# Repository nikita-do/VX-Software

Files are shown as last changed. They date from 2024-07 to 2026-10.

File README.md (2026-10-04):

# Vital-X Software

Vital-X streams ECG, PPG, and EDA/GSR measurements to a Python backend over MQTT. The backend processes the incoming signals, estimates a pain level, and stores measurements for monitoring and later review.

This repository contains the server backend and presentation materials. The project describes a mobile-friendly web interface hosted separately; its source code is  present `software/vitalx_site/`.

## Demo

[Open or download the demo video](https://dvn-resume.vercel.app/assets/projects/vitallog/demo.mp4) (`assets/output.mp4`).

## System Overview

The device sends CBOR-encoded data through an MQTT broker. The backend subscribes to device topics, decodes and validates packets, and passes the signal batches through preprocessing and pain assessment. Raw and processed signals, extracted features, and pain estimates are written to InfluxDB. Pain and pulse-rate estimates are also published over MQTT. When measurement stops, the logger exports processed data to CSV and attempts an optional Google Drive upload; Drive upload is not verified as ready to use without additional setup.

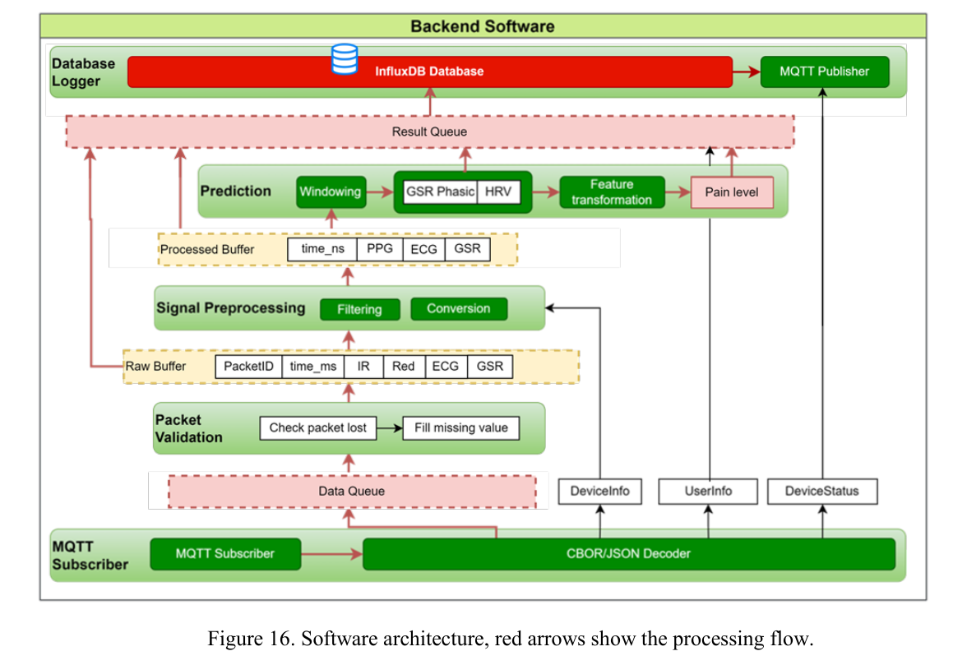
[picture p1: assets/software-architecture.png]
Vital-X backend software architecture and processing flow


The MQTT topic map below shows the device, server, and client communication.

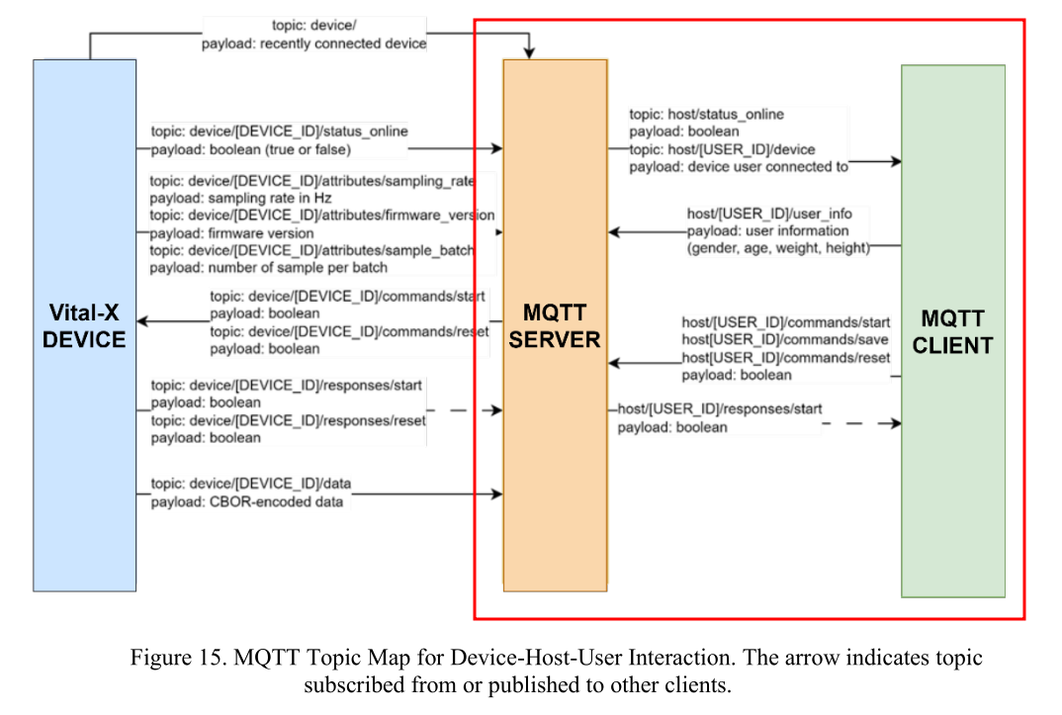
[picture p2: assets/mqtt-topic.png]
Vital-X MQTT topic map


## Remote Device Control

The device is controlled through the [Vital-X web interface](https://vitalx-site.vercel.app/). The device-specific URLs is specified in the `?device=DEVICE_ID` query parameter; replace `DEVICE_ID` with the identifier of the device to control. The interface is used to check device status, submit user information and location, and start or stop data acquisition. Its source code is included but hosted in a separate repository.

## Backend Pipeline

The backend code is in [`software/ServerBackend/`](software/ServerBackend/):

1. `mqtt_subscriber.py` connects to the broker, tracks device status and configuration, decodes CBOR messages, and receives user information.
2. `packet_processor.py` checks packet fields and sample lengths, pads or truncates malformed batch lengths, and handles missing packet IDs. A single missing packet is interpolated; multiple missing packets are represented as missing data.
3. `data_processor.py` converts GSR readings to conductance, filters ECG, PPG, and GSR, estimates pulse rate, and prepares prediction windows.
4. `pain_assessor.py` extracts GSR and HRV features with NeuroKit2 and applies the saved scaler, PCA transform, and voting-classifier model.
5. `database_logger.py` writes raw signals, processed signals, features, and pain estimates to InfluxDB. At the end of a measurement, it exports processed data to CSV and optionally uploads it to Google Drive.
6. `main.py` configures and starts the MQTT subscriber, packet processor, data processor, and database logger.

The prediction window is configured as 5.5 seconds in `main.py`; the thesis describes predictions approximately every five seconds. The project describes the classifier as a five-class ensemble. Classifier training is outside this project's scope.

## Signal Processing and Pain Assessment

The processing below follows the server flow in the thesis (Software Design, p. 18; Signal Preprocessing, p. 22), with implementation-specific settings taken from `data_processor.py` and `data_processor_filters.py`.

### Packet and Signal Preparation

The packet processor checks that incoming `IR`, `RED`, `ECG`, and `GSR` arrays have the expected lengths. The data processor then creates a timestamp for each sample using the device packet time and sampling rate.

The reflective PPG sensor produces inverted waveforms. The backend combines the two optical channels as:

$$
PPG_{avg} = -\frac{IR + RED}{2}
$$

For GSR, the backend converts the sensor voltage to conductance using the voltage-divider relationship implemented in `data_processor.py`:

$$
G_{\mu S} = \frac{10^6}{100{,}000\left(\frac{6600}{V_{mV}} - 1\right)}
$$

Here, the implementation uses a 100 kΩ reference resistance and 6600 mV in the divider expression; multiplying by $10^6$ converts siemens to microsiemens. Conductance is used because it represents the inverse of skin resistance and changes with sweat-related skin response.

### Filter Methodology

The project explains the filter choices as removing slow baseline drift, mains-frequency interference, and faster noise such as motion artifacts while retaining the physiological signal.

| Signal | Method described | Why | Current backend implementation |
| --- | --- | --- | --- |
| ECG | 0.5 Hz high-pass IIR, followed by a 50 Hz (Vietnam) or 60 Hz (Taiwan) FIR notch | Remove baseline drift and local power-line interference | 2nd-order Butterworth high-pass IIR at 0.5 Hz, then a 1025-tap FIR notch. `VN` selects 50 Hz; `TW` and unknown location codes select 60 Hz. |
| PPG | Form the inverted IR/RED average, then 0.5 Hz high-pass IIR and 10 Hz low-pass FIR | Remove baseline wander and attenuate high-frequency noise, including motion artifacts | 2nd-order Butterworth high-pass IIR at 0.5 Hz, then 201-tap FIR low-pass at 10 Hz. |
| GSR/EDA | 3 Hz low-pass FIR | Smooth faster fluctuations while preserving the slower electrodermal response | Convert voltage to conductance, then apply a stateful 513-tap FIR low-pass at 3 Hz. |

The FIR filter states are retained between successive data windows to avoid reinitializing filters at every window boundary. 

#### Why the Backend Uses IIR and FIR

The 2nd-order Butterworth IIR high-pass removes baseline drift efficiently with few coefficients, which suits streaming, but has nonlinear phase. Symmetric FIR low-pass and notch filters are stable and linear-phase, but their tap counts increase computation and delay. At 512 Hz, their group delays are about 1 s for ECG, 195 ms for PPG, and 500 ms for GSR; timestamps are not delay-compensated. 

### Features and Pain Classification

Within `pain_assessor.py`, EDA is decomposed into tonic/phasic components, and the GSR feature set is calculated from the phasic component: peak-to-peak amplitude, maximum, skewness, kurtosis, standard deviation, range, interquartile range, coefficient of variation (SDMN), and standard deviation of successive differences (SDSD).

ECG R-peaks are detected and time-domain HRV features are computed: MeanNN, SDNN, RMSSD, SDSD, and SDRMSSD. These signal features are scaled, projected through the saved PCA transform, and passed to the saved voting-classifier model for each 5.5-second prediction window. Its predicted pain class is published over MQTT and, along with the raw and processed signals and extracted features, written to InfluxDB.

## Run the Backend

### Requirements

- Python and the packages in [`software/ServerBackend/requirements.txt`](software/ServerBackend/requirements.txt)
- An MQTT broker and a Vital-X device publishing the expected device topics
- A reachable InfluxDB instance, organization, bucket, and API token
- The trained model files: `pain_votingclassifier_J.pkl`, `scaler.pkl`, and `pca.pkl`
- The MQTT TLS certificate configured for your broker
- Google Drive OAuth credentials only if Drive export is required

The model files and deployment credentials are not included in this repository. MQTT username/password and the InfluxDB token must be provided through environment variables; the backend exits with an error if they are missing. Configure machine-specific certificate and model paths before running. Never commit live credentials, and rotate any credentials that may already have been exposed in repository history.

### Install

From the repository root:

```bash
python3 -m venv .venv
source .venv/bin/activate
python -m pip install -r software/ServerBackend/requirements.txt
```

Set the MQTT credentials and InfluxDB token in the environment. For example:

```bash
export MQTT_BROKER="your-mqtt-host"
export MQTT_PORT="8883"
export MQTT_USERNAME="your-mqtt-username"
export MQTT_PASSWORD="your-mqtt-password"
export INFLUXDB_TOKEN="your-influxdb-token"
```

Before starting the service, update the InfluxDB URL, organization, and bucket, and point the certificate and model paths in `software/ServerBackend/main.py` to files available on your machine. The code specifies a 512 Hz sampling rate for compatibility with the prediction model.

#### Optional Google Drive Setup

For Drive export, create OAuth client credentials in the Google Cloud Console and enable the Google Drive API. By default, put the downloaded OAuth client JSON at `software/ServerBackend/resources/credentials.json`; the OAuth token is created at `software/ServerBackend/resources/token.json` after the first authorization. Both filenames are ignored by Git. To store either file elsewhere, configure these variables before starting the backend:

```bash
export GOOGLE_CREDENTIALS_PATH="/path/to/google-oauth-client.json"
export GOOGLE_TOKEN_PATH="/path/to/vitalx-drive-token.json"
```

The token parent directory is created automatically. Keep custom credential and token files outside the repository or add their paths to `.gitignore`. Drive authentication alone does not complete the current upload flow: folder initialization is disabled in `database_logger.py`, so enable its `get_or_create_folder()` call before expecting uploads to work.

Start the backend from its directory so its local module imports resolve:

```bash
cd software/ServerBackend
python main.py
```

Stop the service with `Ctrl+C`. The logger writes exported CSV files to `software/ServerBackend/data/`.

## Limitation

The processed signal shows a peak at the beginning of each prediction window. The backend collects fixed, non-overlapping 5.5-second blocks, equivalent to rectangular segmentation, without tapering the signal at block edges. The repeated peak may be a boundary or signal artifact; testing a different window function or overlapping blocks may reduce it, but this has not been verified. Filter state persists across blocks, so the peak should not be assumed to come from resetting the filters. Windowing changes the model input and should be evaluated with recorded data before use.

This is a research prototype, not a clinically validated medical device. The thesis reports that pain-prediction accuracy has not been validated in a clinical setting and identifies ECG lead-off monitoring and real-time pain alerts as unimplemented features.

## See the paper
Ha, Minh-Khue, et al. "VitalLog: Development of a Compact Multimodal Physiological Signal Acquisition System for Tele-Monitoring Applications." Journal of Physics: Conference Series. Vol. 3180. No. 1. IOP Publishing, 2026.

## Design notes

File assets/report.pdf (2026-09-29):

Vietnam National Universities – HCMC International University
School of Biomedical Engineering

## DEVELOPMENT OF A WEARABLE MONITORING DEVICE FOR PAIN ASSESSMENT BASED ON

PHOTOPLETHYSMOGRAPHY,

## ELECTROCARDIOGRAPHY, AND GALVANIC SKIN RESPONSE SIGNALS

By

Do Vy Ngoc

BEBEIU20033

A thesis submitted to the School of Biomedical Engineering in partial fulfillment of the

requirements for the degree of Engineer

Ho Chi Minh city, Vietnam

August - 2025

School of Biomedical Engineering

i

## DEVELOPMENT OF A WEARABLE MONITORING DEVICE FOR PAIN ASSESSMENT BASED ON

PHOTOPLETHYSMOGRAPHY,

## ELECTROCARDIOGRAPHY, AND GALVANIC SKIN RESPONSE SIGNALS

APPROVED BY:

________________________________

Tran Le Giang, PhD., Advisor

________________________________

Nguyen Thi Hiep, Assoc.Prof., Chair

______________________________

Nguyen Thanh Qua, PhD., Reviewer

School of Biomedical Engineering

ii

ACKNOWLEDGEMENT

Over the past nine months, the process of working on this thesis has been both

intellectually stimulating and personally rewarding. Its successful completion would not

have been possible without the invaluable guidance and support of several individuals.

I would like to express my sincere appreciation to Dr. Tran Le Giang for granting

me the opportunity to undertake this project and for providing unwavering support

throughout its duration. This research topic was proposed by MSc. Phan Thien Luan,

Graduate Institute of Biomedical Engineering, National Chung Hsing University, Taiwan,

to whom I am especially grateful for his valuable insights and continuous encouragement

during this work. I am also indebted to Mr. Luu Quy Ha for his contribution in designing

the device’s PCB, and to MSc. Ha Minh Khue for providing thoughtful feedback on the

firmware development. All three, from the Department of Physics and Electronics

Engineering Laboratory, University of Science, Ho Chi Minh City, have provided expert

guidance throughout the implementation of the project.

Finally, I wish to extend my heartfelt gratitude to my parents and family for their

steadfast support and encouragement during this endeavor. Their continued presence and

assistance have been vital to the successful completion of this thesis.

School of Biomedical Engineering

iii

TABLE OF CONTENTS

School of Biomedical Engineering

iv

School of Biomedical Engineering

v

LIST OF FIGURES

Figure 5. Simplify schematic for skin conductance measurement. Electrodes are placed on

Figure 10. Conceptual architecture for implementing the Vital-X device for pain detection

Figure 12. Complete Vital-X device setup, including housing, battery, and wearable

Figure 13. FreeRTOS-based firmware flowchart for data acquisition and publishing..... 14

Figure 14. Circular buffer implementation to store continuous sensor data and CBOR

Figure 16. MQTT Topic Map for Device-Host-User Interaction. The arrow indicates topic

Figure 21. PPG signal processing: IR channel, red channel and derived PPG signals..... 24

School of Biomedical Engineering

vi

Figure 25. Bland-Altman plot comparing HRV measurement from Vital-X and BIOPAC

Figure 27. Correlation between ECG R–R intervals and PPG P-P intervals, by Vital-X. 27

Figure 30. Processed signals plotted by InfluxDB Dashboard, 10-seconds duration....... 29

School of Biomedical Engineering

vii

LIST OF TABLES

Table 2. Decision matrix for wireless communication protocols. Wi-Fi was selected due to

School of Biomedical Engineering

viii

LIST OF ABBREVIATIONS

ECG | Electrocardiography
PPG | Photoplethysmography
GSR | Galvanic Skin Response
SCR | Skin Conductance Response
EDA | Electrodermal Activity
RESP | Respiratory Rate
SpO2 | Saturation of Peripheral Oxygen
HRV | Heart Rate Variability
MQTT | Message Queue Telemetry Transport
TLS | Transport Layer Security
LED | Light-Emitting Diode
IR | Infrared Red
IoT | Internet of Things
BLE | Bluetooth Low Energy
CBOR | Concise Binary Object Representation
ADC | Analog to Digital Converter
I2C | Inter-Integrated Circuit Communication
IIR | Infinite Impulse Response
FIR | Finite Impulse Response

School of Biomedical Engineering

ix

ABSTRACT

Pain remains a significant challenge in both clinical and research contexts due to

the difficulty of objectively detecting it. Traditional assessment methods rely heavily on

patient self-reporting, which may be inaccurate or infeasible, particularly in non-

communicative patients. This thesis presents the design and development of a wearable

acquisition device intended to support a machine learning–based pain detection framework

using electrocardiography (ECG), photoplethysmography (PPG), and galvanic skin

response (GSR) signals.

The proposed device is built around the ESP32-S2 microcontroller, which enables

secure wireless data transmission via the MQTT protocol with TLS encryption.

Physiological signals are acquired in real time and transmitted to a remote server, where a

custom Python application performs signal processing—including filtering, feature

extraction, and pain prediction—along with data visualization and storage. Device control

and configuration are provided through a mobile-friendly web interface.

While the device successfully acquires and transmits high-quality physiological

signals, several features remain unimplemented, including ECG lead-off monitoring and

real-time pain alerts. In addition, the accuracy of the pain prediction model has not yet been

validated in a clinical setting. Despite these limitations, the system establishes a promising

foundation for remote bio-signal monitoring and pain assessment research, with potential

for future clinical integration.

Keywords: Wearable device; Electrocardiography; Photoplethysmography; Galvanic

Skin Response; Pain assessment.

School of Biomedical Engineering

CHAPTER 1.INTRODUCTION

### 1. Introduction to the biomedical problems

### 1.1. Pain – a subjective human experience

Pain is fundamentally a subjective human experience; however, accurately detecting its

onset and levels is crucial for effective clinical assessment and treatment. The International

Association for the Study of Pain defines pain as "an unpleasant sensory and emotional experience

associated with, or resembling that associated with, actual or potential tissue damage" [1]. Unlike

measurable physiological parameters such as blood pressure or temperature, pain cannot be directly

observed or quantified. The pathway of pain involves complex neurophysiological processes that

transmit signals from the periphery to the brain. Historically, pain was equated with nociceptor

response to tissue damage, despite evidence of more complex underlying mechanisms [2]. Acute

pain is short-term, typically lasting from a few days to under six months, and serves as a warning

signal for tissue damage. In contrast, chronic pain persists beyond normal healing, often involving

complex mechanisms and contributing to emotional and physical effects such as anxiety,

depression, and reduced mobility [3].

The accurate assessment of pain is challenging, yet critical. Clinicians must make treatment

decisions—including the type, dosage, and duration of pain relief—based on their understanding

of the patient's pain. Inaccurate assessment can lead to either under-treatment—resulting in

unnecessary suffering—or over-treatment—resulting in increased risk of potentially harmful or

ineffective treatment, especially opioid misuse [4].

### 1.2. Limitations of current pain assessment tools

The current and “gold standard” pain assessment relies on patient self-reporting. A person

uses tools like words, number scales, or pictures with pain scales to describe how much pain they

feel. While giving useful information, self-report has several problems. A person’s pain rating is

subjective and can be affected by their past experiences, thoughts, and behaviors, which are

inconsistent over time. This approach is limited to use for non-communicative individuals, such as

infants, patients under anesthesia, or those with cognitive impairments [5].

Behavioral observation tools are used as alternatives for non-communicative populations.

These tools interpret physiological and behavioral cues—such as facial expressions, body

School of Biomedical Engineering

movements, vocalizations, and consolability—to estimate pain levels. However, observer-based

assessments depend on the skill and judgment of healthcare providers [5]. Both self-report and

behavioral tools provide only a single-point assessment, lacking the ability to monitor pain

continuously or dynamically. These issues show the need for better, more objective ways to assess

pain.

### 2. Analysis of current solutions

### 2.1. Physiological signals for pain detection

Currently, several physiological parameters such as galvanic skin response (GSR), heart

rate, heart rate variability (HRV), respiration rate (RESP), blood pressure, pupillary reflex dilation,

electromyogram, and skin temperature are being explored as proxies for pain [6], [7]. Two most

common indices used for pain assessment in medical devices are the analgesia nociception index,

which is based on HRV and the surgical pleth index, which is based on PPG [7]. GSR provides

valuable information in the indication of pain [6]. The complexity of pain has led researchers to

explore multimodal machine learning-based systems that combine various physiological signals to

classify pain states. Teichmann et al. [8] used ECG and PPG signals with a random forest classifier

for pain detection and Chu et al. [9] combined ECG, PPG, and GSR, applying linear discriminant

analysis, K-nearest neighbor, and support vector machines algorithms. These studies demonstrate

the effectiveness of physiological signals and machine learning in identifying pain.

a. Electrocardiography (ECG)

ECG is a non-invasive technique used to record the electrical activity of the heart over time.

The heart’s rhythm and contraction are regulated by electrical impulses that generate small voltage

changes detectable on the surface of the body. These changes are captured using electrodes placed

on the skin, typically on the chest and limbs.

The simplest form of ECG is a single-lead system. While it lacks the diagnostic capability

of a standard 12-lead ECG, single-lead systems can still capture the complete ECG waveform as

shown in Figure 1. Single-lead ECG enables measurement of R–R intervals, which are used to

compute HRV—a key parameter for detecting physiological responses to pain stimuli.

School of Biomedical Engineering

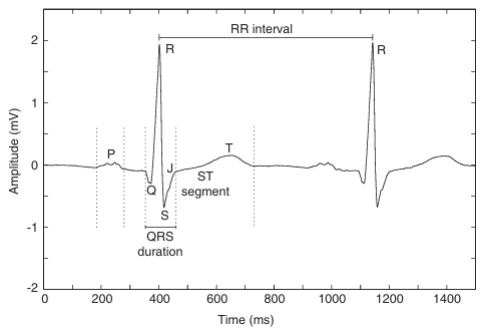
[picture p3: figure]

Figure 1. A normal ECG waveform, with P wave, QRS complex, and T wave [10]

b. Photoplethysmography (PPG)

PPG is a non-invasive optical technique used to detect blood volume changes in the

microvascular bed of tissue. A typical PPG sensor comprises a light source and a photo detector

that measures the amount of light either transmitted through or reflected by the tissue. As blood

volume fluctuates with each heartbeat, the intensity of the detected light changes, producing a

waveform that mirrors the cardiac cycle, as shown in Figure 2.

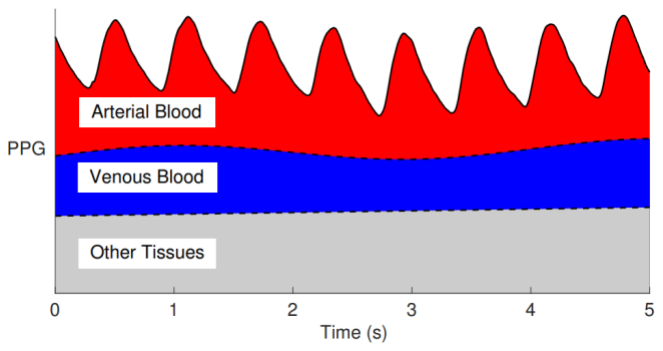
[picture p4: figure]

Figure 2. PPG signal and their simplified origins [11]

There are two main types of optical arrangements: transmissive and reflective. In the

transmissive configuration, the LED and photodiode are positioned on opposite sides of a body

part. In the reflective configuration, both the LED and photodiode are placed on the same side of

the measurement site. Reflective PPG is more suitable for wearable devices and continuous

monitoring due to its flexible placement, while transmissive PPG is often used in clinical-grade

pulse oximeters where higher signal quality is required. PPG is typically used to estimate RESP

School of Biomedical Engineering

and oxygen saturation level (SpO₂). By analyzing the intervals between successive peaks of the

PPG waveform, one can also obtain HRV and R-R intervals.

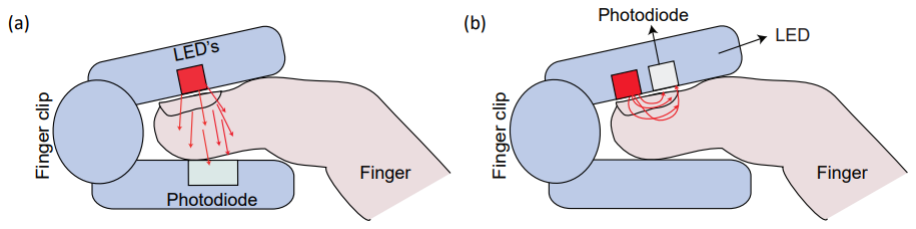
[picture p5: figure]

Figure 3. Transmissive mode (a) and reflectance mode (b) of contact PPG [11]

c. Galvanic skin response (GSR)

GSR, sometime called electrodermal activity (EDA), describes changes in the skin's

electrical conductance caused by sweat gland activity. The tonic level of GSR is called skin

conductance level; and the transient responses within seconds are skin conductance responses

(SCR) [12]. GSR is widely used in psychophysiological research as a non-invasive indicator of

emotional and cognitive arousal, such as stress, fear, or excitement. During emotional arousal, the

sympathetic nervous system activates sweat glands, particularly in areas like the palms and soles,

leading to increased skin moisture. This increases skin conductance, resulting in elevated GSR and

the presence of SCR peaks.

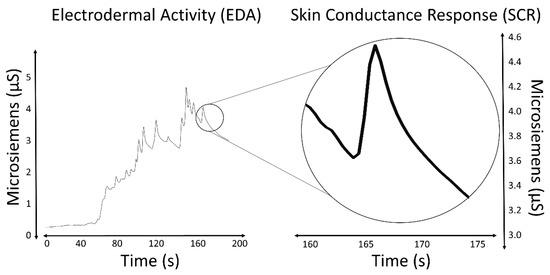
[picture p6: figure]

Figure 4. GSR (or EDA) signal and an isolated SCR [12]

A typical GSR setup involves placing two electrodes on the skin where sweat glands are

densely concentrated, usually on the fingers or palms. Passive voltage-divider circuits are

commonly used, normally with a constant voltage to measure skin conductance. A steady voltage

School of Biomedical Engineering

is applied across electrodes; the resulting current or voltage drop is used to track changes in skin

conductance, as illustrated in Figure 5.

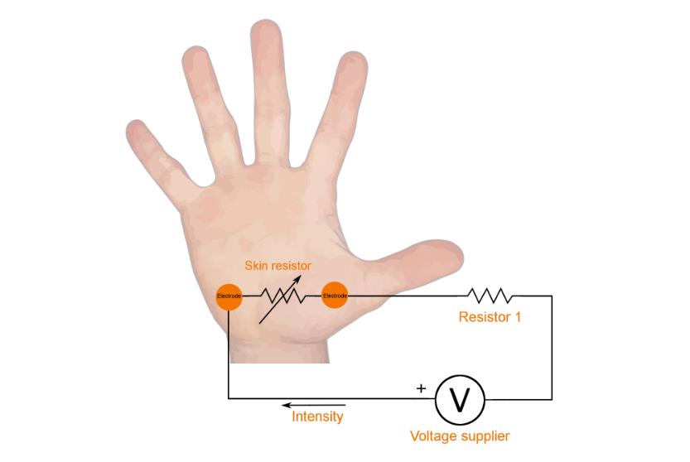
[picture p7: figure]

Figure 5. Simplify schematic for skin conductance measurement. Electrodes are placed on the palms or fingertips [13]

### 2.2. Wearable sensors used in pain detection

Table 1 and Figure 6 summarizes commercialized devices and the physiological parameters

for pain and stress monitoring according to Chen et al [7].

Table 1. Wearable sensors used in pain and stress detection, modified from [7]

Type of Signal | Commercialized Wearable Sensors
Heart activity | Empatica E4 wrist band, AutoSense, Cardiosport TP3, Wahoo chest belt, BioHarness 3
Brain activity | MindWave mobile EEG headset
Muscle activity | DataLOG
Electrodermal activity | Empatica E4 wrist band, BN-PPGED, Q-sensor, Shimmer sensor
Respiratory | AutoSense, SleepSense
Blood volume pulse | Empatica E4 wrist band, BN-PPGED
Body / skin temperature | Empatica E4 wrist band, AutoSense
3-axis accelerometer data | Empatica E4 wrist band, Q-sensor

School of Biomedical Engineering

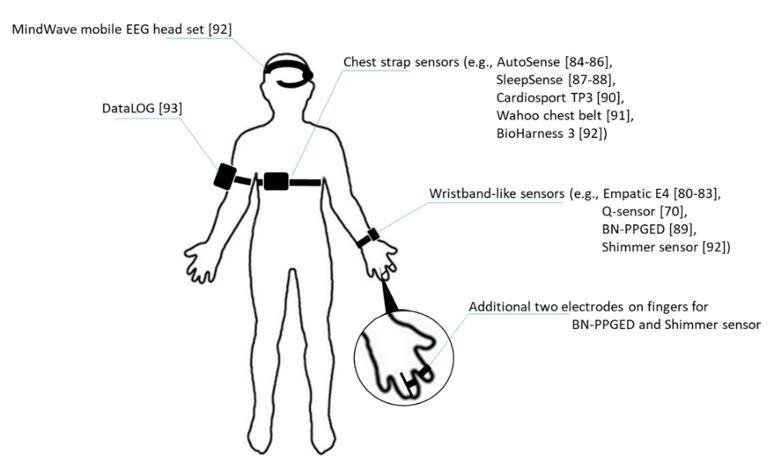
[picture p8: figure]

Figure 6. Illustration of pain and stress sensors placement on human body [11]

According to Table 1, the physiological signals most measured by commercial wearable

devices for stress and pain research include heart activity and electrodermal activity. Blood volume

pulse, measured via PPG, provides insights into cardiovascular dynamics. GSR measurement is

typically performed using wristband-like sensors via two electrodes placed on the fingers to

enhance signal acquisition, as seen with the BN-PPGED and Shimmer sensor.

Among eleven commercialized devices, only four include GSR measurement. Of these,

only the Empatica E4 and BN-PPGED sensors also capture heart rate. The Empatica E4 stores

physiological data in onboard memory for later download during follow-up visits, whereas the BN-

PPGED transmits data wirelessly to a BIOPAC communication station connected to a monitoring

device. While the BN-PPGED offers an ideal setup for pain assessment research, it requires a

dedicated data acquisition model, making it less practical for widespread clinical use.

### 3. Proposed solutions

Although GSR is recognized as a valuable indicator in pain research, its limited clinical

adoption has led to minimal integration into commercial devices alongside other signals, such as

ECG and PPG. To address the gap, the thesis proposes a portable, easily deployable device capable

of collecting ECG, PPG, and GSR signals for physiological data collection in pain assessment.

School of Biomedical Engineering

Besides the two common parameters—ECG and GSR—for pain monitoring, the PPG signal can

provide a more comprehensive view into the patient physiological state by inferring SpO₂, RESP

and can also be combined with ECG to estimate pulse transit time, which serves as an indirect

indicator of real-time blood pressure. Beyond pain monitoring, the proposed device offers broad

applications as a portable physiological data acquisition system, supporting effective health

assessment and personalized care.

### 4. Project goals

The objective of this thesis is to design a low-cost, portable data acquisition device, referred

to as Vital-X, capable of real-time recording of ECG, PPG, and GSR signals. The device wirelessly

transmits raw data to a remote server, where signal processing, feature extraction, and pain

prediction are performed. Furthermore, the device is integrated into a machine learning–based pain

detection framework, demonstrating a complete and easily deployable pain assessment system

suitable for clinical settings.

### 5. Research frameworks

The initial state of the research involves identifying existing challenges in pain

management. The design requirements are then guided by relevant standards and insights from the

literature review. An iterative development process enables refinement through continuous testing

and evaluation. While the full system includes the training and validation of the machine learning

model, this thesis focuses solely on the design of the device and its communication with the remote

server for pain prediction. Figure 7 presents the research process framework that focuses on

embedded system design.

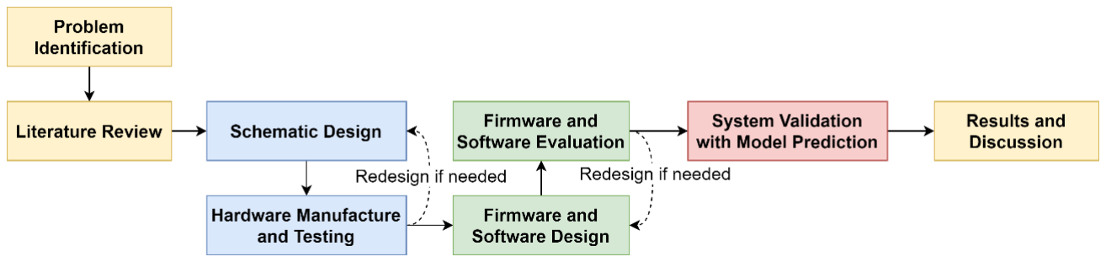
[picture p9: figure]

Figure 7. Research framework diagram.

School of Biomedical Engineering

CHAPTER 2.METHODOLOGY

### 1. System Overview

### 1.1. Networking protocols

Wearable devices rely on networking protocols to enable the transmission of physiological

signals to external systems for processing, storage, and real-time monitoring. Figure 8 describes a

typical IoT-driven system, where patients who require non-invasive monitoring due to their

physiological status can be continuously monitored by the caregivers. The sensor collects the

physiological information from the patient and uses gateways to further transmit the information

to a cloud. This information is then sent to the caregivers wirelessly for monitoring or diagnosis.

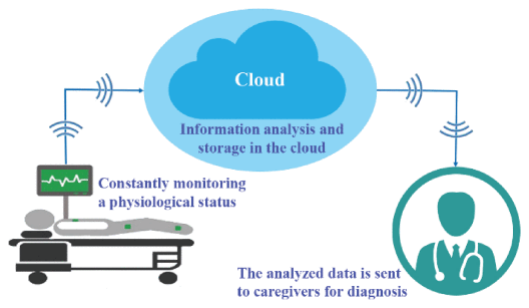
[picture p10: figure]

Figure 8. IoT Device in healthcare Connectivity Model [14]

Same concept was applied to the pain detection system. At the Local Area Network level,

wireless protocols such as Bluetooth Low Energy (BLE), Wi-Fi, and ZigBee are commonly used

to establish short-range connections between wearables and local gateway. In cloud-computing,

where storage and processing happen in large data centers, internet connectivity is essential for

data transmission. The simplest way to achieve this is by using Wi-Fi, eliminating the need for

intermediary gateway devices required in BLE- or ZigBee-based architectures.

School of Biomedical Engineering

Table 2. Decision matrix for wireless communication protocols. Wi-Fi was selected due to its ease of integration and high data throughput.

Protocol | Max Range | Power consumption | Max Data Rate | Cloud integration | Scalability
BLE | 100 m | Low (10 mW) | Moderate (1 Mbps) – suitable for transmitting small sensor data | Indirect via smartphone, which forwards data to the cloud | Moderate – suitable for small networks; limited by star topology
Zigbee | 100 m | Low (35 mW) | Low (250 kbps) – sufficient for periodic sensor updates | Indirect via Zigbee hub/gateway, which connects to the cloud | High – supports large mesh networks with many nodes
Wi-Fi | 200 m | High (1 W) | High (54 Mbps) -enables high-throughput applications | Direct via internet routers | Moderate – access point limits the number of concurrent devices

At the application layers - where software components communicate over the internet -

common protocol stacks include Message Queue Telemetry Transport (MQTT), Hyper Text

Transfer Protocol (HTTP) and Constrained Access Protocol (CoAP). Unlike HTTP, which is

heavyweight, and CoAP, which can struggle with firewalls due to UDP, MQTT offers lightweight,

reliable messaging over TCP, making it the good choice for efficient IoT communication [15],

[16].

MQTT enables efficient communication between devices, or clients, and a central broker—

which routes messages between publishers and subscribers based on topics, as shown in Figure 9.

MQTT features low overhead and includes useful mechanisms such as Quality of Service (QoS),

retained messages and last will messages, with strong community support from brokers such as

Eclipse Mosquitto and HiveMQ.

School of Biomedical Engineering

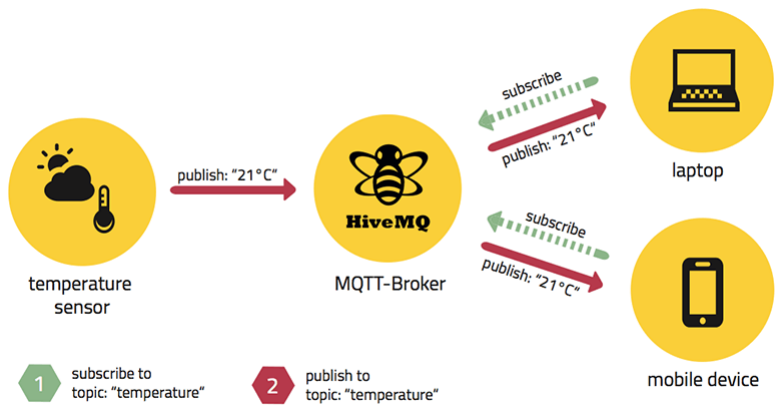
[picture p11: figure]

Figure 9. MQTT communication with PubSub mechanism [17]

### 1.2. Requirement analysis

The requirements for a medical device are typically divided into two main categories:

hardware and firmware/software. Table 3 and Table 4 defines the requirement for the device

firmware and hardware. The requirements follow industry standards for a Class B medical device,

ensuring compliance with safety, usability, and data integrity principles (see Appendix A).

Table 3. Firmware requirements

Requirement | Description | Verification Method | Relevant Standard | Risk references
Signal acquisition | Acquire raw ECG, PPG and GSR at 512Hz | Data log review | IEC 60601-2-47 | Signal distortion
Encrypted data transmission | TLS-encrypted data storage and transmission | Functional testing + Certificate validation | IEC 62304 | Patient data leakage
Wi-Fi disconnection handling | Exponential backoff if transmission fails, maximum of 30-second delay and 5 retries. After that, the device restarts. | Disconnection test | IEC 62366 - Usability | Incomplete or corrupt logs. User confusion
LED indicator | Announce user about Wi-Fi status | Visual inspection | IEC 62366 - Usability | User confusion

School of Biomedical Engineering

Table 4. Software requirements for the mobile application

Requirement | Description | Verification Method | Relevant Standard | Risk references
User interface | Display start and stop buttons to control data acquisition Show prediction result | Visual inspection | IEC 62366 -Usability | User confusion
Collect demographic data | Send user’s age, weight, height, sex to the server | Visual inspection | IEC 60601-2-25:201.12.1.103 | User confusion

Table 3 outlines the embedded firmware requirements for accurate signal acquisition and

reliable transmission. Since the system’s pain prediction model runs on a clinical data sampled at

a high frequency 512 Hz — the device’s sampling rate must match this requirement to ensure data

compatibility and maintain model inference accuracy.

Table 4 presents the requirements for the mobile application, or MQTT client application,

responsible for device control and data visualization. Through this application, observers—such as

nurses, doctors, or administrators—can enter patient demographic information, control the data

acquisition process (start/stop), and observe the predicted pain level results.

Figure 10 illustrates the complete pain detection system following the successful

implementation of the Vital-X device. The device publishes raw ECG, PPG and GSR data to an

MQTT broker. An MQTT server subscribes to the broker to receive the transmitted data, which is

then processed for pain level prediction and display of results on the observer’s mobile phone.

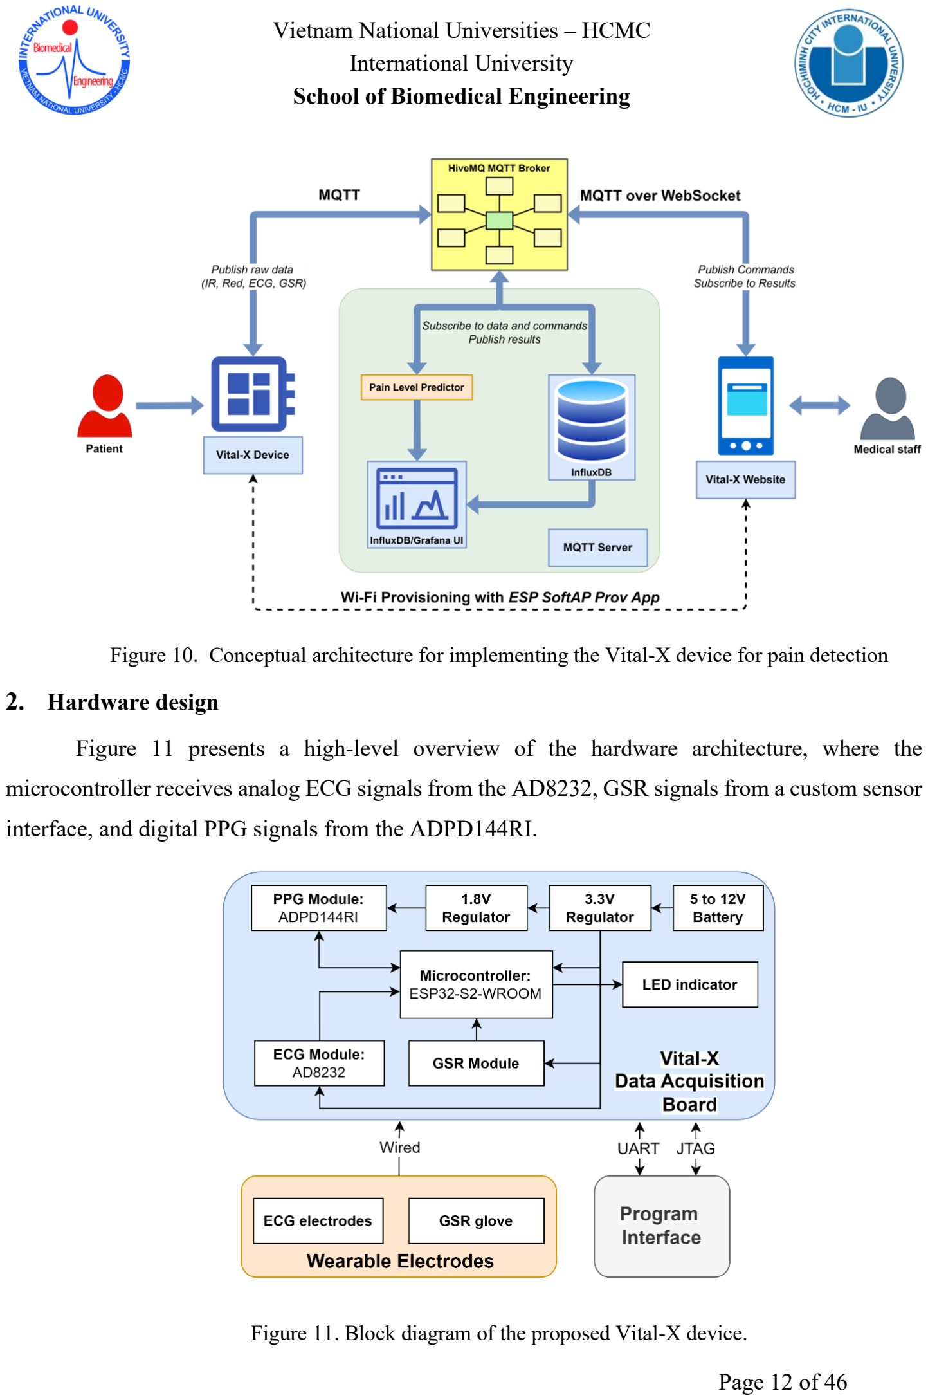
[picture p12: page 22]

School of Biomedical Engineering

Figure 10. Conceptual architecture for implementing the Vital-X device for pain detection

### 2. Hardware design

Figure 11 presents a high-level overview of the hardware architecture, where the

microcontroller receives analog ECG signals from the AD8232, GSR signals from a custom sensor

interface, and digital PPG signals from the ADPD144RI.

Figure 11. Block diagram of the proposed Vital-X device.

School of Biomedical Engineering

ESP32-S2-WROOM is a Wi-Fi microcontroller selected as a main control unit. It features

a 32-bit single-core Tensilica LX7 CPU, integrates 2.4 GHz Wi-Fi, 4 MB of SPI flash, and has

hardware-accelerated security features. An LED indicator provides visual feedback for Wi-Fi

connection status. The device is battery-powered for portability.

The optional use of ESP-PROG program interface via USB-to-UART and JTAG

communication allows serial programming, and advanced in-system debugging capabilities. The

ECG connector interfaces with three Ag/AgCl electrodes to acquire biopotential signals from the

subject. These electrodes, labeled LA (Left Arm), RA (Right Arm), and RL (Right Leg), are placed

on the corresponding limbs. The GSR glove consists of two metal electrode plates positioned on

the subject’s fingers. A strap can be used to wear the device on the wristband. Figure 12 shows the

complete and portable device setup, with battery and wearable electrodes connected to the Vital-X

data acquisition board.

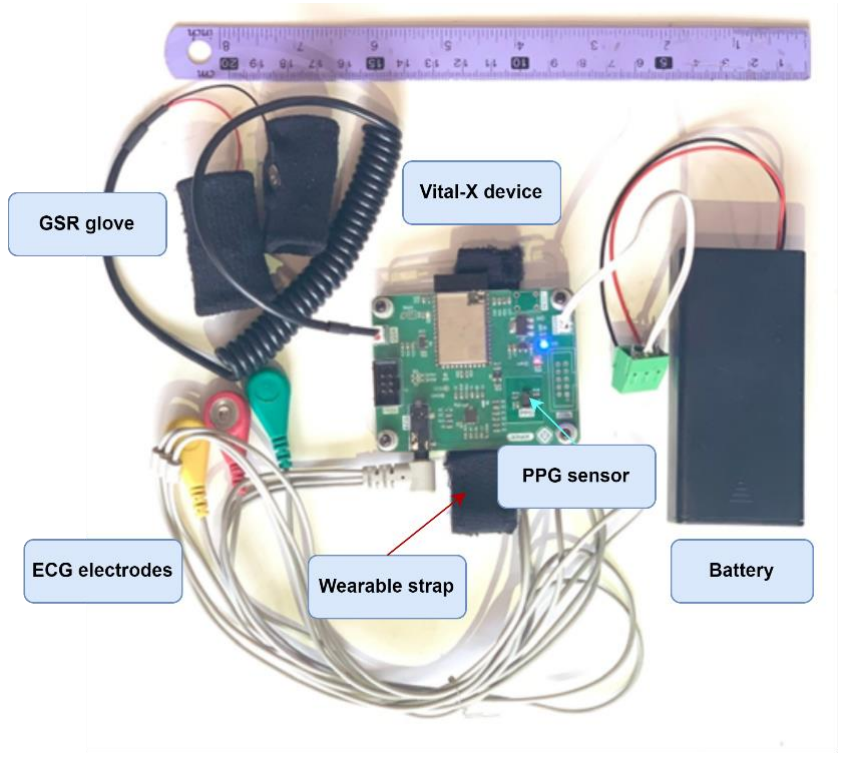
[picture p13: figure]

Figure 12. Complete Vital-X device setup, including housing, battery, and wearable electrodes connected for physiological signal acquisition.

School of Biomedical Engineering

### 3. Firmware design

### 3.1. Task scheduling

FreeRTOS is an open-source, lightweight real-time operation system designed for

microcontrollers and small embedded systems. As shown in Figure 13, FreeRTOS is used to

manage two critical tasks: sensor data acquisition and MQTT-based data transmission. A

FreeRTOS software timer periodically triggers data reading from GSR, ECG and PPG sensors

every 1/512 seconds. Once the number of samples reaches the predefined SAMPLE_BATCH (i.e.,

1536) after 3 seconds, data collection stops, and the system signals the MQTT transmission. The

MQTT publish task retrieves the buffered data, initializes a CBOR encoder, encodes the sample

arrays into a CBOR map, and sends the compressed payload to the MQTT broker.

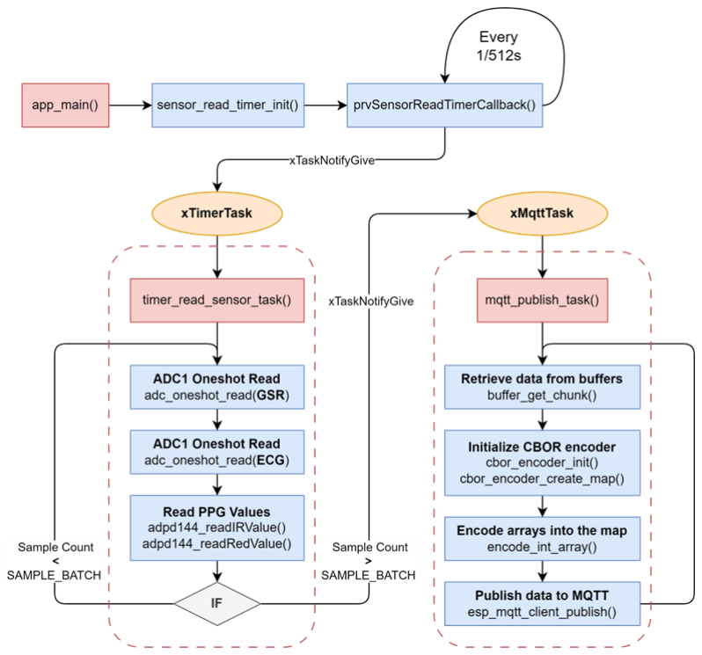
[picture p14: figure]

Figure 13. FreeRTOS-based firmware flowchart for data acquisition and publishing

School of Biomedical Engineering

### 3.2. Data acquisition strategy

The firmware for this project is developed using the Espressif IoT Development Framework

(ESP-IDF), the official development platform for the ESP32. ESP-IDF provides direct access to

low-level features and native support for official examples, making it particularly well-suited for

complex firmware design.

a. Analog-to-Digital Converter (ADC)

The ESP32-S2 features two ADC units, ADC1 and ADC2, which are configured to acquire

signals from the ECG and GSR interfaces respectively.

To maintain precise timing and alignment across all channels, a software timer triggers one-

shot ADC conversions at a fixed sampling rate of 512 Hz. To ensure accuracy, a maximum 12-bit

resolution was chosen. The software calibration is applied to both ADCs to produce more reliable

readings. An 11 dB attenuation setting is configured for both ADC units, allowing each ADC to

support an input voltage range of up to 3300 mV.

b. Inter-Integrated Circuit Communication (I²C)

The ESP32-S2 microcontroller supports two I²C interfaces, one of which is configured as

the master operating in Fast Mode (400 kbit/s) and using a 10-bit addressing scheme for

communication with the ADPD144RI sensor.

The sensor is configured to operate at a sampling rate of 1,000 Hz. To prevent reading

overwritten value from the sensor register, data hold mechanism is employed. The readings from

the infrared (IR) and red (RED) channels are triggered by a software timer at 512 Hz. The

initialsensor setup, including LED power and other configurations, is provided in Appendix C.

c. Data encoding

Concise Binary Object Representation (CBOR) is a data serialization format designed for

efficient message encoding. Unlike text-based formats like JSON or XML, CBOR encodes data in

a compact binary form, reducing transmission size and parsing time. It supports a wide range of

data types including integers, floats, strings, arrays, maps (key-value pairs), and even tagged data

for semantic interpretation. CBOR-encoded MQTT messages enable fast, lightweight, and

interoperable data exchange, ideal for bandwidth- and memory-constrained environments.

School of Biomedical Engineering

d. Buffering technique

To store continuous data from three sensors, a circular buffer implementation was selected.

A circular buffer is a fixed-size, First-In-First-Out data structure that uses a continuous memory

block with separate read and write pointers.

Inside the firmware application, there are four circular buffers which continuously receive

incoming sensor data. The circular buffer has a fixed size of 2048 bytes and operates in a

wraparound manner: when the buffer is full, new samples overwrite the oldest entries without

interrupting the data stream. This design enables concurrent data collection and transmission

without overwriting unread data. The buffer operation, integrated with CBOR encoding for

transmission, is illustrated in Figure 14.

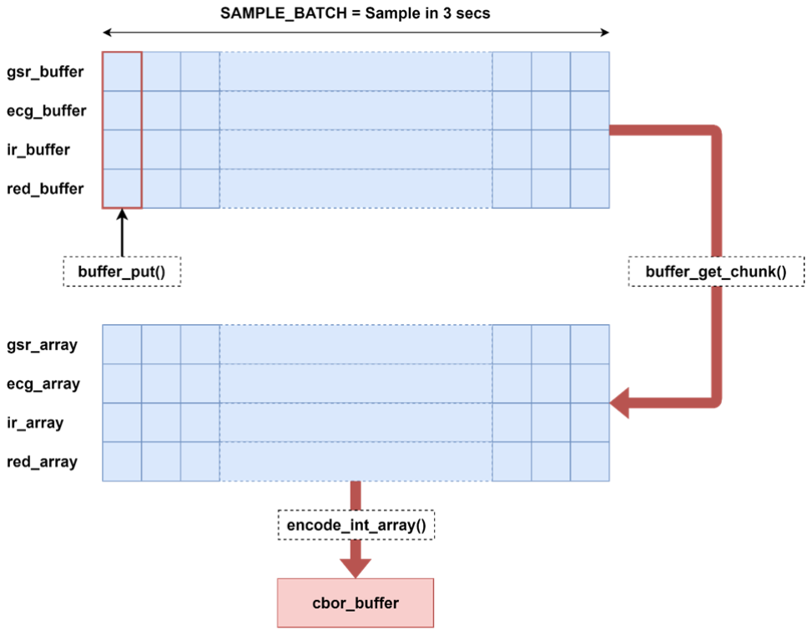
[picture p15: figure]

Figure 14. Circular buffer implementation to store continuous sensor data and CBOR encoding before publishing 3-second data packet over MQTT

At fixed intervals of every 3 seconds, a function named buffer_get_chunk() is triggered to

extract a snapshot of the most recent data points stored in the circular buffer. The extracted data,

consisting of integer sensor readings, is then passed to the encoding function, which serializes the

dataset into a compact CBOR format, awaiting transmission.

School of Biomedical Engineering

### 3.3. Data transmission

a. Wi-Fi connectivity

The Vital-X device features an automated Wi-Fi connection and recovery mechanism to

ensure reliable network access and MQTT communication. On power-up, it attempts to reconnect

to the last known Wi-Fi network using credentials stored in the ESP32’s Non-Volatile Storage

(NVS). If unsuccessful, it enters provisioning mode, indicated by the onboard LED blinking at

500 ms intervals. A LED indicator serves as the main guide for users to understand the device’s

connection status. If the connection is later lost, the device retries connection while the LED blinks

at 200 ms intervals. After five failed attempts, it clears the NVS and re-enters provisioning mode

for reconfiguration. A solid LED indicates a successful connection.

To differentiate devices running the same firmware, each unit was assigned a unique

identifier derived from the last three bytes of its Wi-Fi MAC address, prefixed with ‘VX’. This

device ID also serves as the device’s Wi-Fi network name. ESP32 Wi-Fi provisioning is performed

with Security Level 2 using X25519 key exchange, AES-CTR encryption, and HMAC-SHA256

authentication. This provides protection against Man-in-the-Middle attacks and eavesdropping,

common risks when connecting to unsecured Wi-Fi networks. Provisioning is done via soft access

point (SoftAP) Wi-Fi mode of the ESP32 using ESP SoftAP Provisioning application. This app is

used to send Wi-Fi Network credentials, including network name and password to the ESP32

devices.

b. MQTT messaging

The ESP32 device subscribes to the MQTT command topic to receive commands from the

broker. These commands control the start or stop of sensor data acquisition remotely. The device

publishes responses and sensor readings to device status and data topics using QoS 0 for minimal

latency. To monitor the device's availability, the firmware uses the Last Will and Testament to

automatically update the device’s status (e.g., "offline") after 1 minute of device’s disconnection.

Retained Messages retain the last known status for the patient’s information and device parameters

setting.

School of Biomedical Engineering

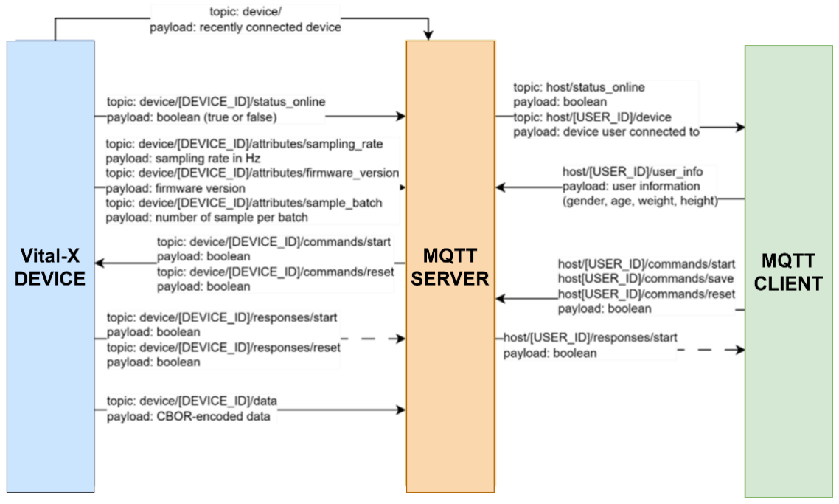
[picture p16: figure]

Figure 15. MQTT Topic Map for Device-Host-User Interaction. The arrow indicates topic subscribed from or published to other clients.

### 4. Software design

A Python application was developed on the server side. Figure 16 illustrates the data flow

within the server, showing how raw data (ECG, IR, RED, and GSR) from the device is processed

for pain prediction. After decoding and checking for packet loss, the raw data underwent

mathematical conversion. For GSR, the voltage values (in millivolts) were converted to skin

conductance (in microsiemens, µS) using a theoretical formula, shown in Appendix B.

Since the PPG sensor operates in a reflectance configuration, the captured signals—

comprising both IR and RED channels—represented an inverted view of the PPG waveform. The

combined PPG signal was computed using the formula:

PPGavg = −

IR + RED
2

The processed signals were then passed into the pain prediction module for feature

extraction and classification every 5 seconds. For GSR, the extracted features included: amplitude,

School of Biomedical Engineering

maximum value, skewness, kurtosis, standard deviation, range, interquartile range (IQR), standard

deviation of mean (SDMN), and standard deviation of successive differences (SDSD).

For ECG, HRV features were extracted, including: mean R-R interval (MeanNN), standard

deviation of R-R intervals (SDNN), root mean square of successive differences (RMSSD), SDSD,

and standard deviation of root mean square successive differences (SDRMSSD).

All feature extraction procedures were performed using the NeuroKit2 library [19]. The

resulting features were input into a five-class ensemble classifier. The classifier combined outputs

from multiple models using a voting mechanism to predict the corresponding pain level. Results

— including raw data, processed signals, extracted features, and predicted pain levels — were

logged into InfluxDB, a locally hosted time-series database, for both storage and real-time

monitoring. Pain level was then published to the user interface.

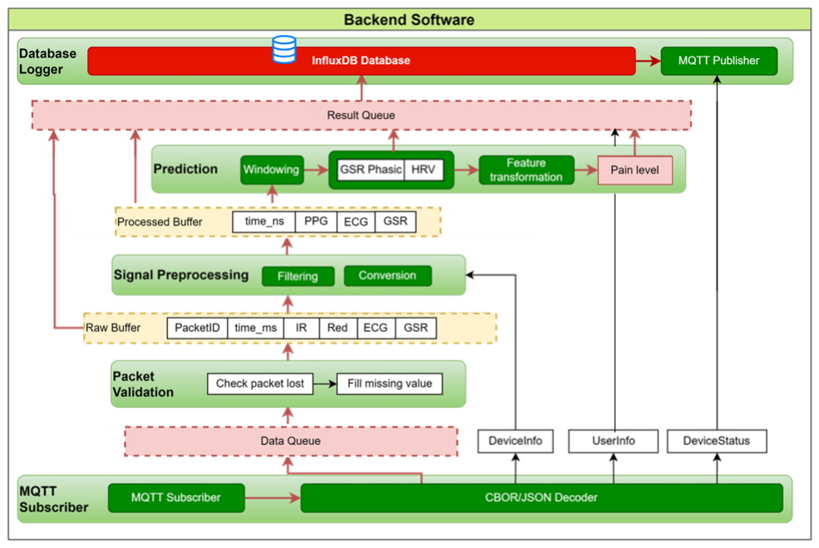
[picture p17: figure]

Figure 16. Software architecture, red arrows show the processing flow.

School of Biomedical Engineering

### 5. User Interface

The device is wirelessly configured, monitored, and controlled through a web interface

hosted on Vercel, a cloud platform for deploying serverless web applications. Each device is

accessible via a unique URL containing a query parameter ?device=DEVICE_ID.

Figure 17 illustrates how medical staff can input patient information and specify the

measurement location (Taiwan or Vietnam) through the device’s web interface. This website also

enables control of data acquisition, displays the device’s connection status (online/offline), and

provides predicted pain level.

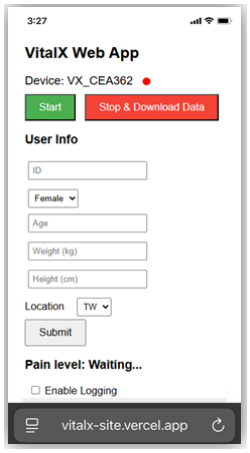
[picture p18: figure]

Figure 17. VitalX website for user interface.

Using ESP SoftAP Provisioning application, users can connect to Vital-X’s SoftAP for Wi-

Fi provisioning using either a device-specific QR code or a manual Wi-Fi connection process.

Successful provisioning is indicated when the LED indicator on the Vital-X remains solid. Figure

18 illustrates the steps for observers to provision, control, and monitor the device.

School of Biomedical Engineering

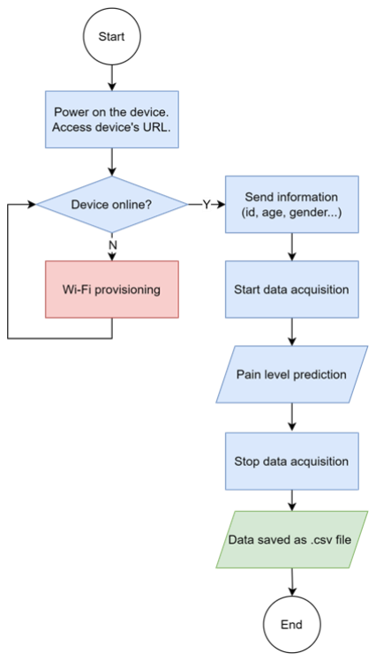
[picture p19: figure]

Figure 18. User guidelines for control and monitoring the device’s operation

### 6. Test Setup and Evaluation Strategy

### 6.1. Equipment and Environment

The Vital-X device was tested with an ECG cable connected, using Skintact F-TB1

Ag/AgCl electrodes on the author’s body. The BIOPAC MP160 system served as the reference for

signal testing, and an ESP-PROG USB-to-UART interface was used for serial data logging.

A running server, a mobile phone with ESP SoftAP Provisioning and a Wi-Fi hotspot were

required to test device’s functionality.

### 6.2. Test Procedures

School of Biomedical Engineering

a. Signal Preprocessing

The ECG, GSR, and PPG signals were filtered using Neurokit’s filter designs. For the ECG

signal, a high-pass IIR filter at 0.5 Hz was applied to remove baseline drift, followed by a 50 Hz

(for Vietnam) and 60 Hz (for Taiwan) notch FIR filter to suppress power-line interference. The

PPG signal—obtained as the inverted combination of the RED and IR channels—was processed

with a high-pass IIR filter at 0.5 Hz to correct for baseline wander and a low-pass FIR filter at 10

Hz to attenuate high-frequency noise such as motion artifacts. The GSR signal was filtered using

a low-pass FIR filter at 3 Hz. A plot was generated to compare the raw and processed signals,

demonstrating the improvements achieved through signal processing.

b. ECG Signal Evaluation

The device’s ECG electrodes were connected to a human subject simultaneously with a

BIOPAC system for comparative measurement. Following the American Heart Association

standards for torso ECG measurement, the arm electrodes were positioned in the infraclavicular

fossae medial to the deltoid insertions, while the left leg electrode was placed midway between the

costal margin and the iliac crest along the left anterior axillary line [20]. The skin was cleaned and

gently abraded before electrode attachment.

ECG recordings from both devices were manually time-aligned for comparability. HRV

from each device was quantified using the SDNN, calculated over three successive RR intervals.

Bland Altman plot was used to visualize any systematic bias and the range of agreement between

the devices. This method plots the average of the two measurements against their difference,

Average =

Xi + Yi
2

Difference =

Xi − Yi
2

And the bias is the mean difference between the two measurements methods, calculated by:

Bias =

1
n

∑(Xi − Yi)

n

i=1
Where Xi

is the measurement from method 1, Yi is measurement from method 2 and n is

the total number of paired observations.

School of Biomedical Engineering

The Limit of Agreement indicates the expected range for 95% of the differences between

the two methods, with

Upper Bound (UB) = Bias + 1.96 × SD

Lower Bound (LB) = Bias − 1.96 × SD

Where Standard deviation (SD) of differences measures the spread of variability of the

differences.

SD = √
1
n − 1

∑[(Xi − Yi
) − Bias]

2

n

i=1

c. PPG Signal Evaluation

For PPG, observations were made regarding the morphology of the waveform, specifically

the prominence and shape of the systolic and diastolic peaks. To evaluate the consistency between

cardiac features derived from ECG and PPG, R–R intervals obtained from ECG were compared

with peak-to-peak intervals extracted from PPG. A correlation plot was generated to assess the

relationship between the two measurements, providing a validation step for PPG-derived inter-beat

interval estimation. Neurokit provides the algorithm to calculate the R-R interval. Simple peak

detection algorithm was used to calculate the peak-to-peak interval from the PPG.

d. GSR Signal Evaluation

GSR measurement was evaluated by connecting precision resistors (e.g. 100 kΩ, 470 kΩ,

1 MΩ and 10MΩ) across the input terminals. For each resistor, the output was recorded over 10

seconds and averaged to obtain the mean value. The measured GSR values were plotted against

the known resistors, and agreement between the measured data points and the theoretical curve was

assessed.

e. Performance Test

To validate the device stability and assess signal drift, a fixed resistor of 1 MΩ was

connected across the GSR input. GSR values were recorded every minute over a period of 8 hours,

under moderate Wi-Fi conditions, from –40 to –50 dBm. A scatter plot was generated to identify

any trends or deviations indicating drift in the signal over time. Additional functional tests were

conducted in accordance with the requirements outlined in Table 3 and Table 4.

School of Biomedical Engineering

CHAPTER 3.Results

### 1. Signal Processing

Raw signals acquired from Vital-X device include infrared (IR) and red (RED) channels,

as shown in Figure 19(a) and Figure 19(b). These waveforms reflect pulse wave activity but do not

resemble a standard PPG waveform due to the sensor’s reflective configuration. Figure 19(c) shows

the raw PPG signal obtained by taking the inverted average of the IR and RED signals. A filter was

then applied to the raw PPG signal to remove the slowly declining DC component, enhancing the

visibility of the pulsatile component associated with cardiac activity.

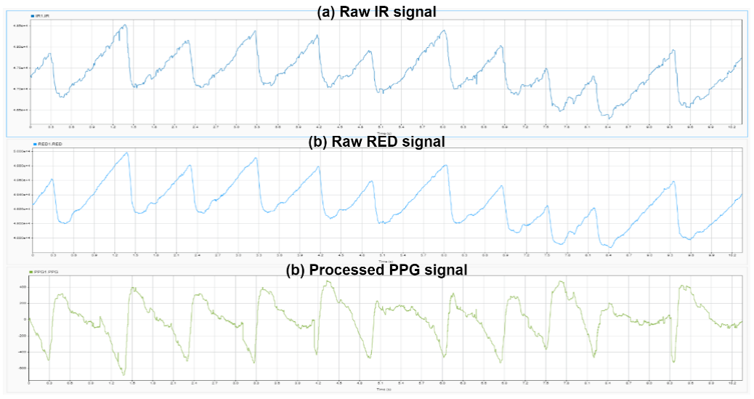
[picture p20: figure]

Figure 19. PPG signal processing: IR channel, red channel and derived PPG signals

Figure 20 and Figure 21 shows a clear improvement in signal quality after filtering. Figure

20 presents the raw ECG output from the AD8232 sensor which is heavily contaminated by high-

frequency noise, shows the improved ECG signal after applying digital notch filters at 50 Hz and

100 Hz, targeting power-line noise and its harmonic.

School of Biomedical Engineering

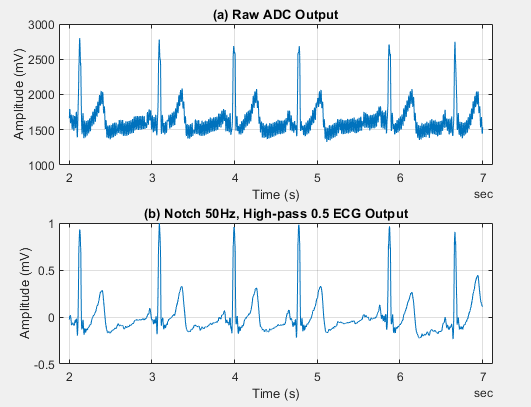
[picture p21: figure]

Figure 20. ECG signal processing: Raw and filtered.

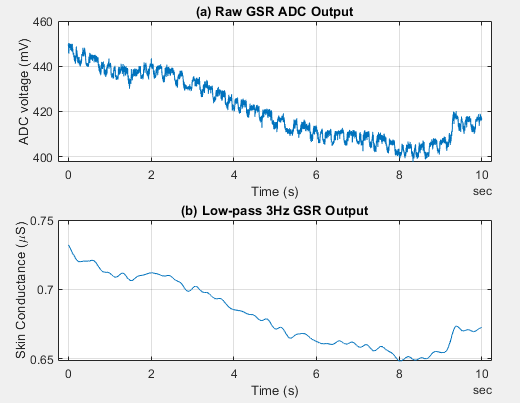
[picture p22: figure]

Figure 21. GSR signal processing: Raw and filtered

### 2. ECG Signal Evaluation

Figure 22 shows the ECG waveforms recorded from BIOPAC and Vital-X on the same

plot, showing similar waveform shapes between the two devices. The Bland–Altman plot indicates

strong agreement between the devices’ algorithm, with a small bias of 11 µs and a narrow upper

and lower limits of agreement at 127 µs and –105 µs, respectively.

School of Biomedical Engineering

Figure 22. Overlay plot of ECG acquisition by Vital-X and BIOPAC.

Figure 23. Bland-Altman plot comparing HRV measurement from Vital-X and BIOPAC

School of Biomedical Engineering

### 3. PPG Signal Evaluation

Figure 24 compares PPG signal and ECG signal recorded simultaneously. The PPG

waveform shows key features like the systolic peak and diastolic notch. tRR denotes the R-R

interval, while tPP represents the interval between two consecutive systolic peaks in PPG. A close

match between tRR and tPP values was observed. Figure 25 shows a strong correlation (R = 0.955)

between ECG R–R intervals and PPG peak-to-peak intervals, with a mean absolute percentage

error (MAPE) of 3.19%.

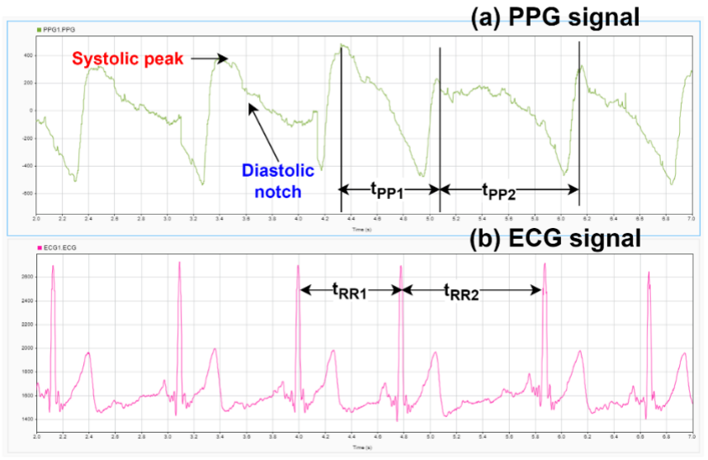
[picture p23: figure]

Figure 24. PPG and ECG signals acquired simultaneously using Vital-X

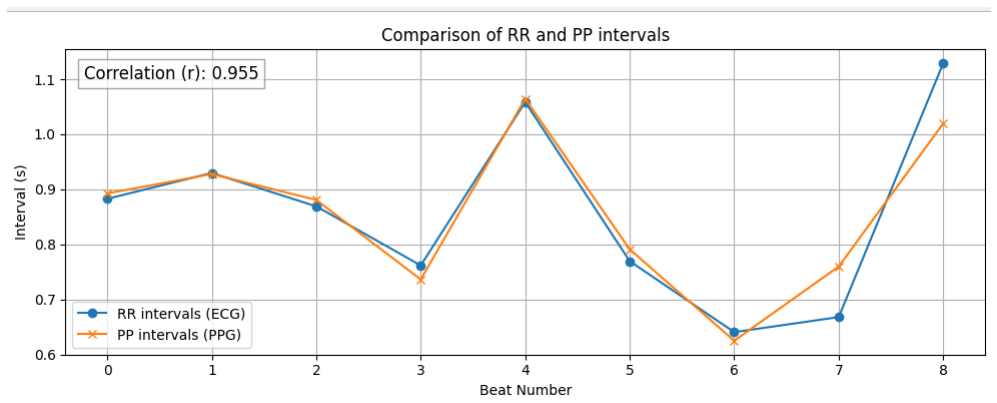
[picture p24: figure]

Figure 25. Correlation between ECG R–R intervals and PPG P-P intervals, by Vital-X.

School of Biomedical Engineering

### 4. GSR Signal Evaluation

Figure 26 illustrates the relationship between input resistance and GSR voltage. A constant

reading at resistance values less than 100 kΩ suggesting ADC saturation at 2583 mV. The mean

absolute percentage error of all measurements is 1.25%, indicating high accuracy between theory

and measurement.

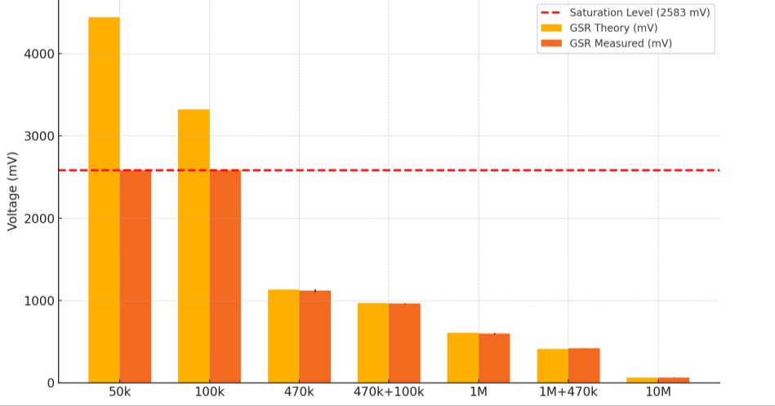
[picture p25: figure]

Figure 26. GSR signal measurements compared to theory

### 5. Performance Test

Figure 27 presents the variation of GSR measurements recorded using the Vital-X device

over a period of 8 hours. Each blue circle represents an individual GSR reading plotted every

minute. The red line indicates the mean GSR value. The time-series plot of the signal showed no

observable trend, with no packet loss. The GSR readings demonstrated high stability over an

extended period, with a mean deviation of just 0.14 mV.

The Vital-X device is capable of remotely communicating with a server, continuously

transmitting data packets of 3-second intervals in real time. Figure 28 presents the InfluxDB

dashboard on the server side, which displays real-time bio-signal visualization and pain prediction

results.

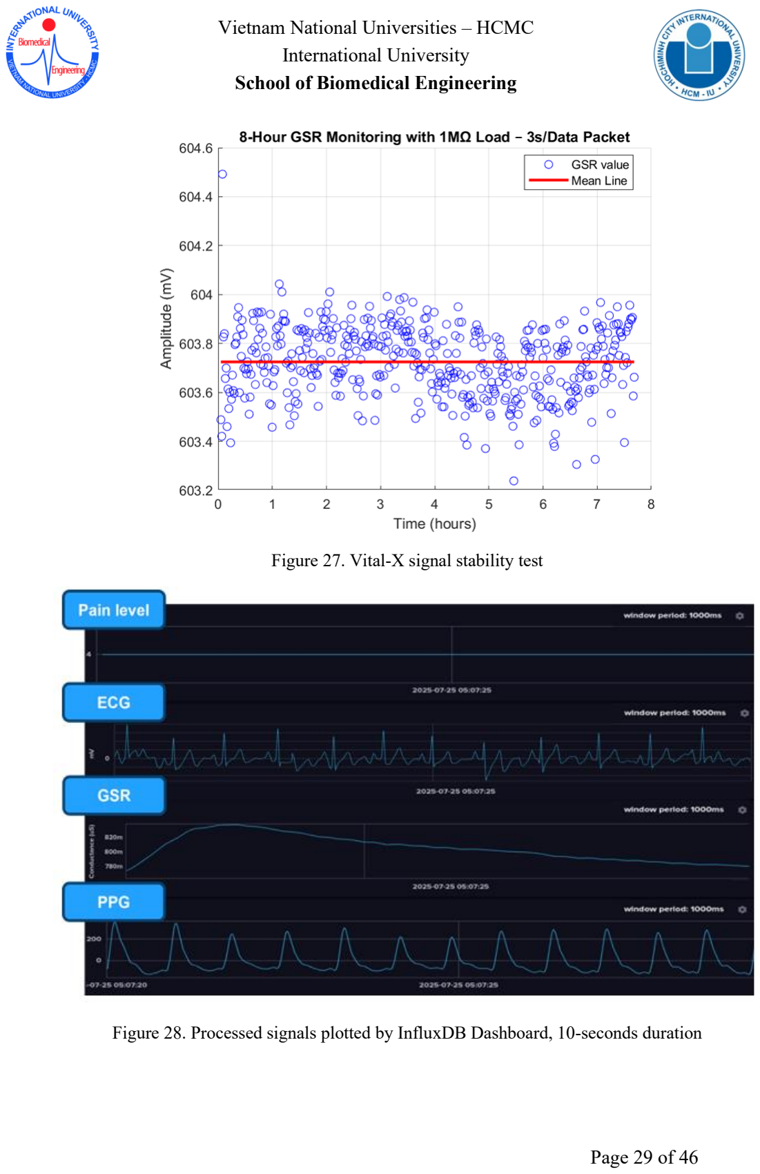
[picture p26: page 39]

School of Biomedical Engineering

Figure 27. Vital-X signal stability test

Figure 28. Processed signals plotted by InfluxDB Dashboard, 10-seconds duration

School of Biomedical Engineering

CHAPTER 4.DISCUSSION

The Vital-X device demonstrates several strengths as a low-cost, real-time physiological

monitoring system for pain detection. A key advantage lies in its ability to reliably transmit data

via Wi-Fi, achieving no packet loss over an 8-hour period. This direct communication with a

remote server eliminates the need for intermediate gateways, which are commonly required by

commercial devices that rely on short-range Bluetooth and local data storage. By offloading

computational tasks such as feature extraction and machine learning inference to the server, Vital-

X maintains efficient performance despite its limited onboard processing resources.

The quality of acquired physiological signals supports the system’s reliability for pain

assessment. HRV extracted from ECG recordings closely aligned with results from a reference

BIOPAC system, as confirmed by Bland–Altman analysis. Similarly, PPG peak intervals showed

strong correlation with ECG R–R intervals, validating PPG-derived inter-beat estimation. The

custom-designed GSR module yielded stable readings consistent with theoretical expectations.

In contrast to compact wristband devices such as the Empatica E4, Vital-X requires more

cumbersome electrode placement for both ECG and GSR acquisition. Moreover, the absence of an

onboard accelerometer makes the device more vulnerable to motion artifacts, limiting its suitability

to contexts in which patients remain immobile, such as during surgical procedures or post-

anesthesia care unit stays.

Another limitation is ADC saturation in the GSR measurement circuit. When using low-

resistance values (e.g., 100 kΩ), the output voltage reaches the ADC’s maximum of 2.853 V,

resulting in signal clipping and loss of meaningful data. This threshold is relatively high for typical

human skin resistance, ranging from 25 kΩ to 1 MΩ [21], especially under conditions of high sweat

gland activity.

Overall, these findings indicate that Vital-X can provide reliable, high-quality physiological

data streams suitable for real-time feature extraction and vital sign monitoring. By combining stable

wireless transmission, efficient server-based processing, and accurate bio-signal acquisition, the

system demonstrates strong potential for deployment in clinical settings where cost-effective and

scalable pain monitoring solutions are required.

School of Biomedical Engineering

CHAPTER 5.CONCLUSION.

### 1. Summary of the research development

This thesis presents the design and implementation of Vital-X, a low-cost, portable data

acquisition device aimed at real-time pain detection using physiological signals. The system

captures raw ECG, PPG, and GSR signals at a sampling rate of 512 Hz and transmits the data via

Wi-Fi to a remote machine learning inference server for signal processing, feature extraction, and

pain prediction. Device control and Wi-Fi provisioning are managed through a mobile phone

website and application, while MQTT is used as the messaging infrastructure to ensure real-time

communication among the device, the server and the mobile phone.

### 2. Limitations

Several limitations constrain the practicality and clinical applicability of the device.

Reliable operation depends on stable Wi-Fi connectivity, which in hospital environments may

require dedicated access points or room-specific hotspots. The use of two separate mobile

applications—for Wi-Fi provisioning and device control—further adds to the complexity of the

user experience. In addition, key features remain unimplemented, including ECG lead-off detection

and real-time pain alert functionality, which limits both the safety and clinical utility of the system.

Finally, the accuracy of the pain prediction model has not yet been validated, underscoring the need

for further evaluation and refinement.

### 3. Suggestion and future application

Despite existing challenges, the proposed system architecture lays the groundwork for

several promising directions, including continuous pain monitoring to guide medication adjustment

and optimize patient care. Future work could further enhance the system’s flexibility, scalability,

and clinical integration by enabling interoperability with electronic health records via HL7/FHIR

standards, thereby facilitating seamless data exchange within clinical workflows. In addition, the

device could be extended to infer other vital signs, such as heart rate, blood pressure, SpO₂, RESP,

and body temperature from the ECG and PPG signals. These developments would strengthen the

device's role as a comprehensive physiological monitoring platform and support broader adoption

in diverse clinical contexts.

School of Biomedical Engineering

REFERENCES

[1] International Association for the Study of Pain (IASP), “IASP Announces Revised Definition

of Pain,” ISAP News. Accessed: July 08, 2025. [Online]. Available: https://www.iasp-

pain.org/publications/iasp-news/iasp-announces-revised-definition-of-pain/

[2] B. Nicholson, “Differential diagnosis: nociceptive and neuropathic pain,” Am. J. Manag. Care,

vol. 12, no. 9 Suppl, pp. S256-262, June 2006.

[3] K. P. Grichnik and F. M. Ferrante, “The difference between acute and chronic pain,” Mt. Sinai
J. Med. N. Y., vol. 58, no. 3, pp. 217–220, May 1991.
[4] M. Boltz, Ed., Evidence-based geriatric nursing protocols for best practice, 4th ed. New York:

Springer Pub. Co, 2012.

[5] K. Herr et al., “Pain Assessment in the Nonverbal Patient: Position Statement with Clinical

Practice Recommendations,” Pain Manag. Nurs., vol. 7, no. 2, pp. 44–52, June 2006, doi:

10.1016/j.pmn.2006.02.003.

[6] R. Fernandez Rojas et al., “Multimodal physiological sensing for the assessment of acute pain,”

Front. Pain Res., vol. 4, p. 1150264, June 2023, doi: 10.3389/fpain.2023.1150264.

[7] J. Chen, M. Abbod, and J.-S. Shieh, “Pain and Stress Detection Using Wearable Sensors and

Devices—A Review,” Sensors, vol. 21, no. 4, p. 1030, Feb. 2021, doi: 10.3390/s21041030.

[8] D. Teichmann, J. Klopp, A. Hallmann, K. Schuett, S. Wolfart, and M. Teichmann, “Detection

of acute periodontal pain from physiological signals,” Physiol. Meas., vol. 39, no. 9, p. 095007,

Sept. 2018, doi: 10.1088/1361-6579/aadf0c.

[9] Y. Chu, X. Zhao, J. Han, and Y. Su, “Physiological Signal-Based Method for Measurement of

Pain Intensity,” Front. Neurosci., vol. 11, p. 279, May 2017, doi: 10.3389/fnins.2017.00279.

[10] L. Sörnmo and P. Laguna, “Electrocardiogram (ECG) Signal Processing,” in Wiley

Encyclopedia of Biomedical Engineering, 1st ed., M. Akay, Ed., Wiley, 2006. doi:

10.1002/9780471740360.ebs1482.

[11] “Photoplethysmography signal processing and synthesis,” in Photoplethysmography,

Elsevier, 2022, pp. 69–146. doi: 10.1016/b978-0-12-823374-0.00015-3.

School of Biomedical Engineering

[12] H. F. Posada-Quintero and K. H. Chon, “Innovations in Electrodermal Activity Data

Collection and Signal Processing: A Systematic Review,” Sensors, vol. 20, no. 2, p. 479, Jan.

2020, doi: 10.3390/s20020479.

[13] | “Galvanic | Skin | Response,” | Tobii. | [Online]. | Available:

https://connect.tobii.com/s/article/galvanic-skin-response-gsr?language=en_US

[14] F. T. Al-Dhief et al., “A Survey of Voice Pathology Surveillance Systems Based on Internet

of Things and Machine Learning Algorithms,” IEEE Access, vol. 8, pp. 64514–64533, 2020,

doi: 10.1109/ACCESS.2020.2984925.

[15] | C. | Ian, | “MQTT | Vs. | HTTP | for | IoT,” | HiveMQ. | [Online]. | Available:

https://www.hivemq.com/blog/mqtt-vs-http-protocols-in-iot-

iiot/?utm_source=YouTube&utm_medium=Video&utm_campaign=MQTT+vs+HTTP+in+Io

T

[16] | C. | Ian, | “MQTT | vs | CoAP | for | IoT,” | HiveMQ. | [Online]. | Available:

https://www.hivemq.com/blog/mqtt-vs-coap-for-iot/

[17] HiveMQ Team, “MQTT Publish/Subscribe Architecture (Pub/Sub) – MQTT Essentials:

Part 2,” HiveMQ. [Online]. Available: https://www.hivemq.com/blog/mqtt-essentials-part2-

publish-subscribe/

[18] Espressif, ESP SoftAP Provisioning. (July 18, 2025). Espressif. [Online]. Available:

https://play.google.com/store/apps/details?id=com.espressif.provsoftap&pcampaignid=web_s

hare

[19] D. Makowski et al., “NeuroKit2: A Python toolbox for neurophysiological signal

processing,” Behav. Res. Methods, vol. 53, no. 4, pp. 1689–1696, Aug. 2021, doi:

10.3758/s13428-020-01516-y.

[20] P. Kligfield et al., “Recommendations for the Standardization and Interpretation of the

Electrocardiogram,” Circulation, vol. 115, no. 10, pp. 1306–1324, Mar. 2007, doi:

10.1161/CIRCULATIONAHA.106.180200.

[21] W. Prokasy, Electrodermal Activity in Psychological Research. Elsevier, 2012.

School of Biomedical Engineering

APPENDICES

Appendix A. Requirement Analysis for a Class II Wearable Device with Class B software

Requirement | Description | Acceptance Criteria
IEC 60601-1 Safety | Electrical safety, thermal safety, mechanical safety, data safety, electromagnetic compatibility | Patient leakage current: <10 uA Enclosure leakage current <100 uA Insulation resistance > 5 MOhm Temp: < 41 – 43 C for contact area No sharp edge, has adjustable strap Encrypted data storage and transmission No failures during immunity testing
IEC 62304 -Software development | Software development, risk management, configuration management | Software safety classification Version control, development environmental setup, task management. Functional and non-functional requirements. System block diagram, Modular software architecture Programming language, Coding standards, error handling strategy Unit, integration and system testing Identify software hazards and mitigations (ISO 14971) Version identifier & Changelog Appendix for traceability matrix
IEC 62366 -Usability engineering | Human factors and safety-related usability | Intended users, use environment Potential use errors, potential harm and implement risk controls by UI or instructions
IEC 60601-2-47 – Ambulatory ECG | ECG signal fidelity, Data recording and storage, Lead systems | Bandwidth: 0.05 Hz – 100 Hz; sampling rate ≥ 200 Hz ADC resolution: ≥ 10 bits Timing accuracy: drift < 1 second over 24 hours RR detection error: ≤ ±5 ms compared to reference Data loss: 0% during normal operation Input impedance: Specifies battery performance and safety under extended operation Proper lead labeling, color-coding, and secure connection Lead disconnection detection
ISO 80601-2-61 – Pulse oximeter | Relevant safety and performance clauses for heart rate monitoring | Pulse rate accuracy: ±3 bpm or ±3%, whichever is greater Sampling rate: ≥ 25–50 Hz (raw PPG) LED power safety

School of Biomedical Engineering

Appendix B. Vital-X Schematics and GSR theoretical curve

School of Biomedical Engineering

Appendix C. ADPD144 PPG sensor initial register configuration

Register Address | Value | Register Name | Description
0x10 | 0x0001 | Mode | Set to 0x0001 to enable writing to registers.
0x02 | 0x0005 | INT_IO_CTL | Enables interrupt drive, active low.
0x11 | 0x30A9 | SLOT_EN | Enables FIFO drop if full. Time Slot A & B = sample mode with 32-bit sum.
0x12 | 0x0001 | F_SAMPLE | Sample rate = 1000 Hz.
0x14 | 0x0116 | PD_LED_SELECT | PD1–PD4 to Channel 3 & 4; Time Slot A & B active; LED2 pulses in A, LED1 in B.
0x15 | 0x0330 | NUM_AVG | Average 8 samples in Time Slot A and B.
0x18 | 0x3FFF | SLOTA_CH1_OFFSET | Not used (max value 16383).
0x19 | 0x3FFF | SLOTA_CH2_OFFSET | Not used (max value 16383).
0x1A | 0x1FF0 | SLOTA_CH3_OFFSET | Offset = 8176 (half-scale).
0x1B | 0x1FF0 | SLOTA_CH4_OFFSET | Offset = 8176 (half-scale).
0x1E | 0x3FFF | SLOTB_CH1_OFFSET | Not used (max value 16383).
0x1F | 0x3FFF | SLOTB_CH2_OFFSET | Not used (max value 16383).
0x20 | 0x1FF0 | SLOTB_CH3_OFFSET | Offset = 8176 (half-scale).
0x21 | 0x1FF0 | SLOTB_CH4_OFFSET | Offset = 8176 (half-scale).
0x23 | 0x3005 | ILED1_COARSE | Scale 100%, driver current = 100 mA.
0x24 | 0x3007 | ILED2_COARSE | Scale 100%, driver current = 130 mA.
0x25 | 0x0207 | ILED_FINE | LED1 & LED2 fine timing = 593.75 ns.
0x30 | 0x0319 | SLOTA_LEDMODE | Pulse offset A = 25 µs, pulse width = 3 µs.
0x31 | 0x0813 | SLOTA_NUMPULSES | Pulse period A = 19 µs, pulse count = 8.
0x35 | 0x0319 | SLOTB_LEDMODE | Pulse offset B = 25 µs, pulse width = 3 µs.
0x36 | 0x0813 | SLOTB_NUMPULSES | Pulse period B = 19 µs, pulse count = 8.
0x39 | 0x21F3 | SLOTA_AFEMODE | AFE fine offset = 593.75 ns, AFE offset = 15 µs, AFE width = 4 µs.
0x3B | 0x21F3 | SLOTB_AFEMODE | AFE fine offset = 593.75 ns, AFE offset = 15 µs, AFE width = 4 µs.
0x42 | 0x1C36 | SLOTA_GAIN | TIA = 50k, band-pass = 390kHz/100kHz, VREF = 1.265V, integrator = 200k/6.33pF.
0x44 | 0x1C36 | SLOTB_GAIN | Same as Slot A Gain.
0x4E | 0x0040 | ADC_TIMING | ADC clock only pulses during conversion.
0x10 | 0x0002 | Mode | Set to 0x0002 to run the device.

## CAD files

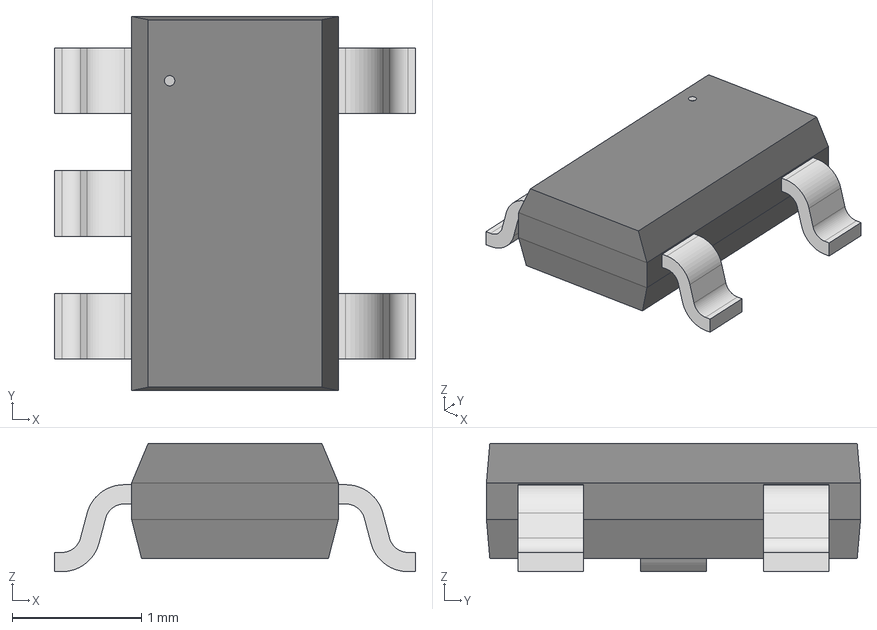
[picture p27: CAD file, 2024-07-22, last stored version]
hardware/customLib/ADP160AUJZ-1-8-R7/ADP160AUJZ-1-8-R7.step
2.79 x 2.90 x 0.993 mm

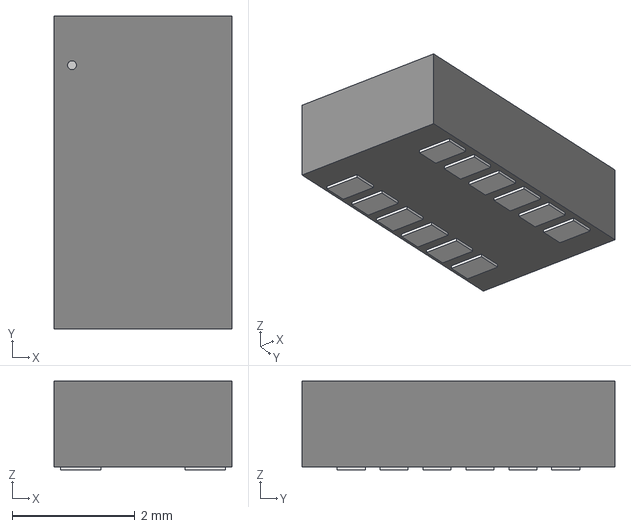
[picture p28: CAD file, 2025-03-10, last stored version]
hardware/customLib/ADPD144RI/CE-12-2_ADI.step
2.90 x 5.11 x 1.45 mm

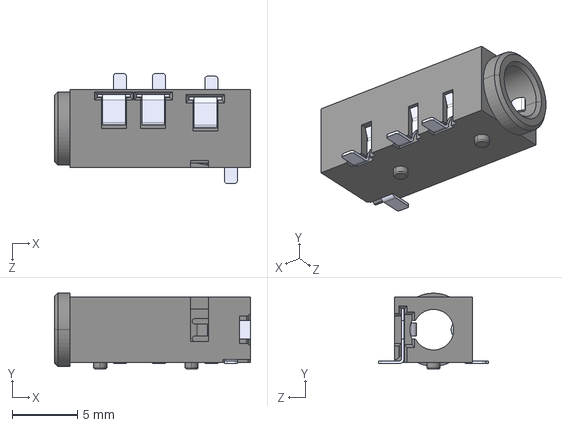
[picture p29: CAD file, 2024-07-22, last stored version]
hardware/customLib/AUDIO/SJ2-3574A-SMT-TR/SJ2-3574A-SMT-TR.step
15.0 x 5.80 x 8.40 mm

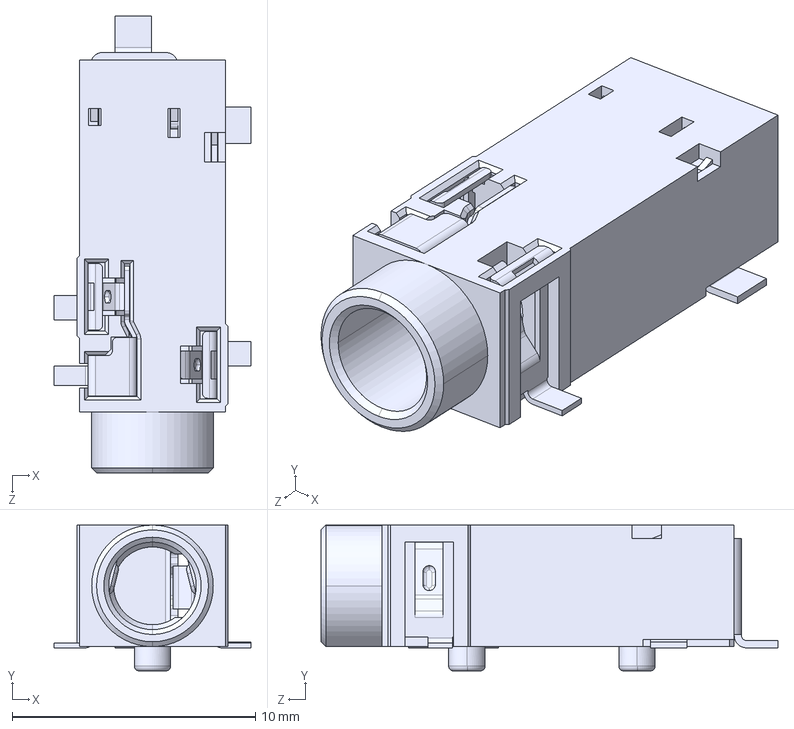
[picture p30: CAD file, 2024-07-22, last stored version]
hardware/customLib/AUDIO/SJ2-3593D-SMT-TR/SJ2-3593D-SMT-TR.step
8.10 x 6.00 x 18.8 mm

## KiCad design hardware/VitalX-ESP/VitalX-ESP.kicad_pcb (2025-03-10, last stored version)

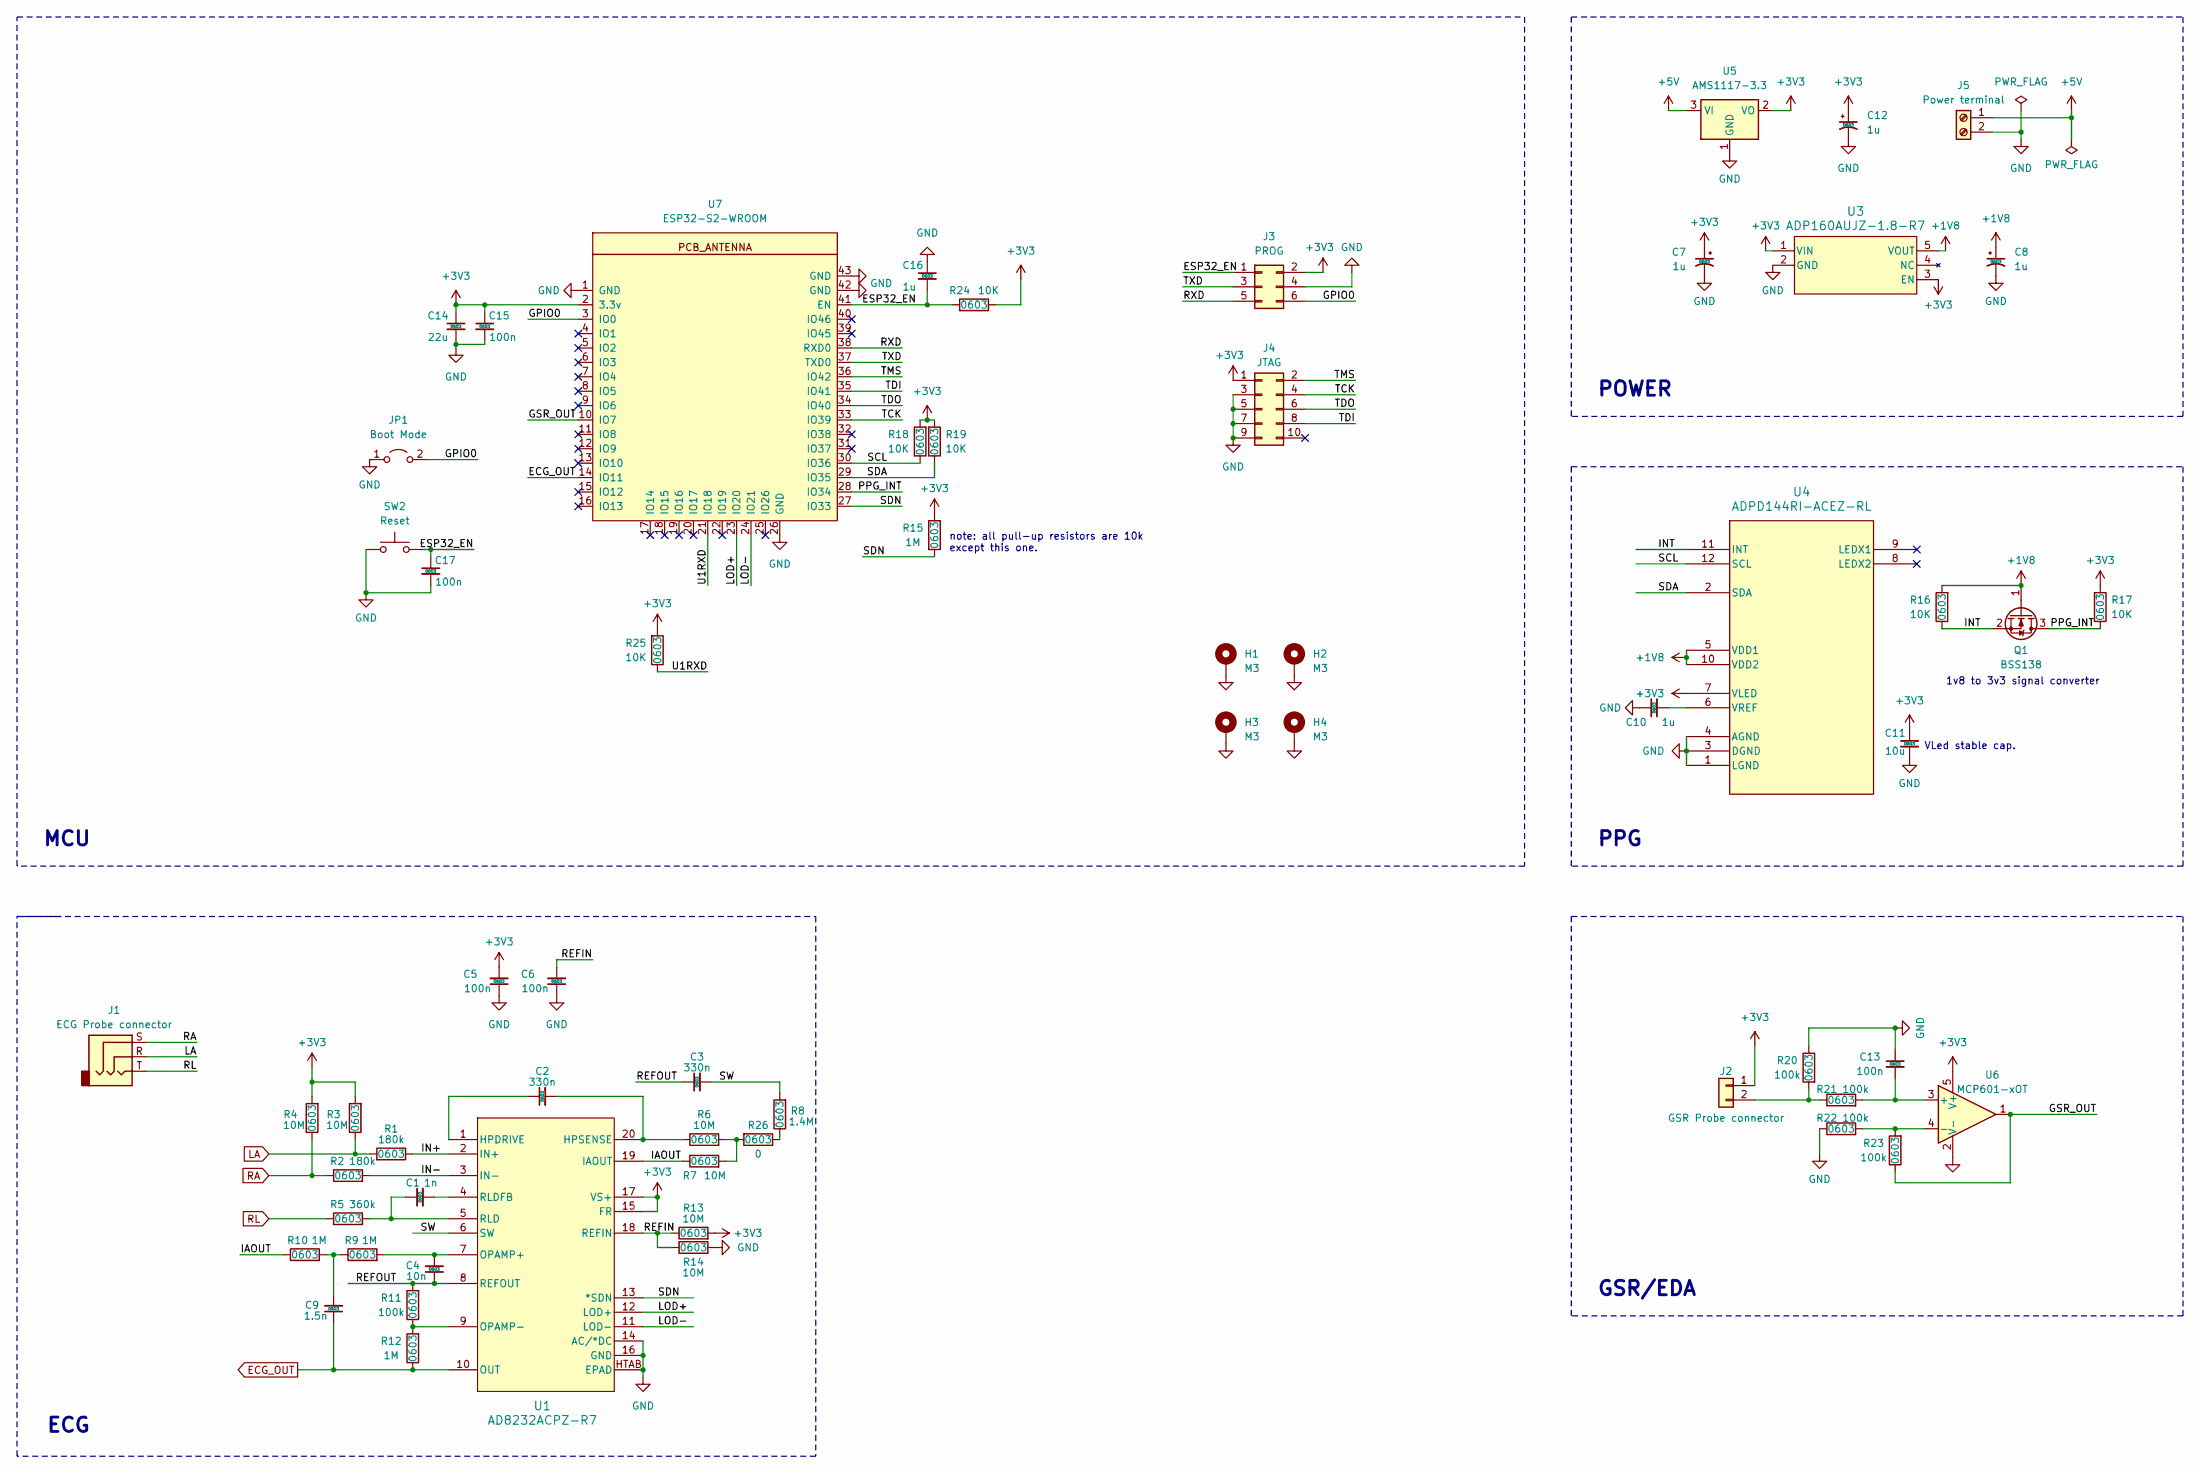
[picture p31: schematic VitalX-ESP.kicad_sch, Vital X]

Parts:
C1: 1n; C_0603_1608Metric
C2, C3: 330n; C_0603_1608Metric
C4: 10n; C_0603_1608Metric
C5, C6, C13, C15, C17: 100n; C_0603_1608Metric
C7, C8, C10, C12, C16: 1u; C_0603_1608Metric
C9: 1.5n; C_0603_1608Metric
C11: 10u; C_0603_1608Metric
C14: 22u; C_0603_1608Metric
H1, H2, H3, H4: M3; MountingHole_3.2mm_M3_Pad_Via
J1: ECG Probe connector; SJ2-3593D-SMT-TR
J2: GSR Probe connector; PinHeader_1x02_P2.54mm_Vertical
J3: PROG; PinHeader_2x03_P2.54mm_Vertical
J4: JTAG; PinHeader_2x05_P2.54mm_Vertical
J5: Power terminal; TerminalBlock_bornier-2_P5.08mm
JP1: Boot Mode; PinHeader_1x02_P2.54mm_Vertical
Q1: BSS138; SOT-23; mouser mnf num 512-BSS138
R1, R2: 180k; R_0603_1608Metric
R3, R4, R6, R7, R13, R14: 10M; R_0603_1608Metric
R5: 360k; R_0603_1608Metric
R8: 1.4M; R_0603_1608Metric
R9, R10, R12, R15: 1M; R_0603_1608Metric
R11, R20, R21, R22, R23: 100k; R_0603_1608Metric
R16, R17, R18, R19, R24, R25: 10K; R_0603_1608Metric
R26: 0; R_0603_1608Metric
SW2: Reset; SW_Tactile_SPST_NO_Straight_CK_PTS636Sx25SMTRLFS
U1: AD8232ACPZ-R7; AD8232ACPZ; mouser mnf num 584-AD8232ACPZ-R7
U3: ADP160AUJZ-1.8-R7; ADP160AUJZ-1-8-R7; mouser mnf num 584-ADP160AUJZ-1.8R7
U4: ADPD144RI-ACEZ-RL; CE-12-2_ADI; mouser mnf num 584-ADPD144RI-ACEZRL
U5: AMS1117-3.3; SOT-223-3_TabPin2; mouser mnf num 926-LM1117MPX3.3NOPB
U6: MCP601-xOT; SOT-23-5; mouser mnf num 579-MCP601RT-E/OT
U7: ESP32-S2-WROOM; esp32-s2-wrooom; mouser mnf num 356-ESP32S2WRMI320US

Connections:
+1V8: C8.1, Q1.1 (G), R16.2, U3.5 (VOUT), U4.5 (VDD1), U4.10 (VDD2)
+3V3: C5.2, C7.1, C11.1, C12.1, C14.1, C15.1, J2.1, J3.2, J4.1, R3.2, R4.2, R13.2, R15.2, R17.2, R18.2, R19.2, R24.1, R25.2, U1.15 (FR), U1.17 (VS+), U3.1 (VIN), U3.3 (EN), U4.7 (VLED), U5.2 (VO), U6.5 (V+), U7.2 (3.3v)
+5V: J5.1, U5.3 (VI)
/ESP32_EN: C16.2, C17.1, J3.1, R24.2, SW2.2, U7.41 (EN)
/GPIO0: J3.6, JP1.2 (B), U7.3 (IO0)
/GSR_OUT: R23.1, U6.1, U7.10 (IO7)
/IAOUT: R7.1, R10.1, U1.19 (IAOUT)
/IN+: R1.1, U1.2 (IN+)
/IN-: R2.2, U1.3 (IN-)
/INT: Q1.2 (S), R16.1, U4.11 (INT)
/LOD+: U1.12 (LOD+), U7.23 (IO20)
/LOD-: U1.11 (LOD-), U7.24 (IO21)
/PPG_INT: Q1.3 (D), R17.1, U7.28 (IO34)
/REFIN: C6.2, R13.1, R14.1, U1.18 (REFIN)
/REFOUT: C3.1, C4.1, R11.2, U1.8 (REFOUT)
/RXD: J3.5, U7.38 (RXD0)
/SCL: R18.1, U4.12 (SCL), U7.30 (IO36)
/SDA: R19.1, U4.2 (SDA), U7.29 (IO35)
/SDN: R15.1, U1.13 (*SDN), U7.27 (IO33)
/SW: C3.2, R8.2, U1.6 (SW)
/TCK: J4.4, U7.33 (IO39)
/TDI: J4.8, U7.35 (IO41)
/TDO: J4.6, U7.34 (IO40)
/TMS: J4.2, U7.36 (IO42)
/TXD: J3.3, U7.37 (TXD0)
/U1RXD: R25.1, U7.21 (IO18)
ECG_OUT: C9.1, R12.1, U1.10 (OUT), U7.14 (IO11)
GND: C5.1, C6.1, C7.2, C8.2, C10.1, C11.2, C12.2, C13.1, C14.2, C15.2, C16.1, C17.2, H1.1, H2.1, H3.1, H4.1, J3.4, J4.3, J4.5, J4.7, J4.9, J5.2, JP1.1 (A), R14.2, R20.1, R22.1, SW2.1, U1.14 (AC/*DC), U1.16 (GND), U1.HTAB (EPAD), U3.2 (GND), U4.1 (LGND), U4.3 (DGND), U4.4 (AGND), U5.1 (GND), U6.2 (V-), U7.1 (GND), U7.26 (GND), U7.42 (GND), U7.43 (GND)
LA: J1.R, R1.2, R3.1
unnamed: C9.2, R9.1, R10.2
unnamed: J2.2, R20.2, R21.1
unnamed: R8.1, R26.1
unnamed: R6.2, R7.2, R26.2
unnamed: C2.1, U1.1 (HPDRIVE)
unnamed: C2.2, R6.1, U1.20 (HPSENSE)
unnamed: C4.2, R9.2, U1.7 (OPAMP+)
unnamed: R11.1, R12.2, U1.9 (OPAMP-)
unnamed: C1.1, R5.2, U1.5 (RLD)
unnamed: C1.2, U1.4 (RLDFB)
unnamed: C10.2, U4.6 (VREF)
unnamed: C13.2, R21.2, U6.3 (+)
unnamed: R22.2, R23.2, U6.4 (-)
RA: J1.S, R2.1, R4.1
RL: J1.T, R5.1

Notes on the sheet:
MCU
PPG
1v8 to 3v3 signal converter
GSR/EDA
ECG
VLed stable cap.
note: all pull-up resistors are 10k except this one.
POWER

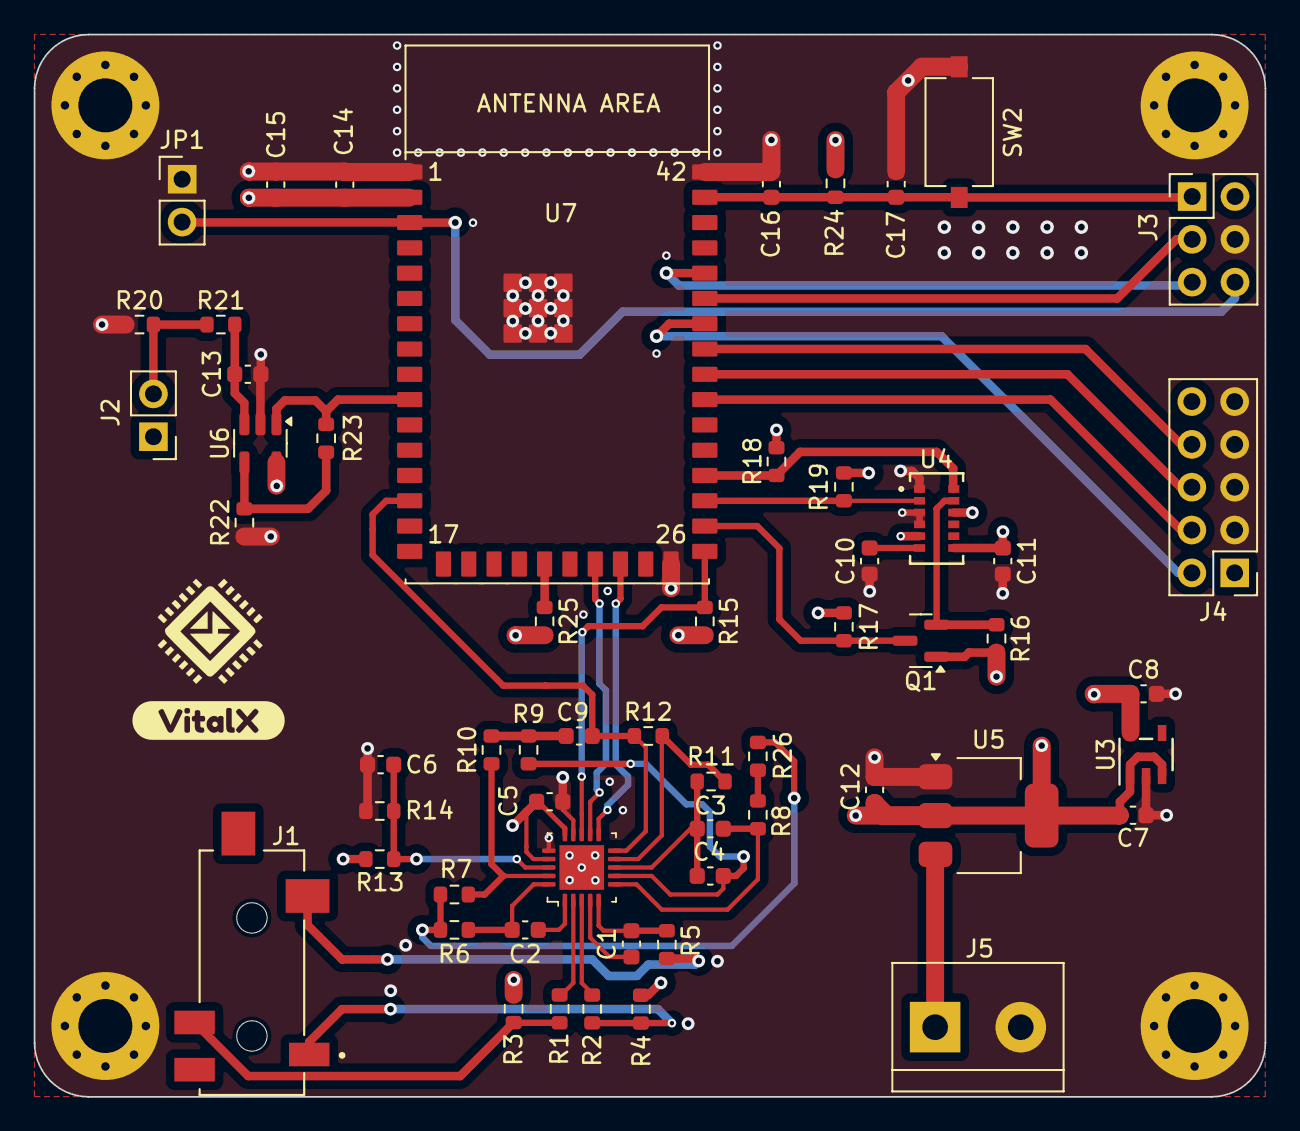
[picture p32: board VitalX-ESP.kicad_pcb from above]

Board: 4 copper layers, 73.0 x 63.0 mm, 62 parts (0 on the bottom side), 44 nets.

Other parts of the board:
kibuzzard-673C1CE7: G***; kibuzzard-673C1CE7

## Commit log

2024-07-22 Init hardware project
    [AD8232ACPZ-R7.STEP, ADP160AUJZ-1-8-R7.step, SJ2-3574A-SMT-TR.step, SJ2-3593D-SMT-TR.step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]
2024-07-25 [VTX-5] Finalize ECG Block. Minor changes: - Remove cache, bak files. - Change AD8232's EPAD electrical type for ERC. - Update footprint path.
    [VitalX-ESP.kicad_sch]
2024-08-05 [VTX-6] Add symbol/footprint.
    Added ADPD144RI PPG symbol and footprint.
    [CE-12-2_ADI.step]
2024-08-05 [VTX-6] Initialize PPG Block.
    Initial implementation of ADPD144RI.
    [VitalX-ESP.kicad_sch]
2024-08-24 [VTX-6] Finalize PPG Block.
    Included AMS1117-3.3V voltage regulator.
    Increased Vled capacitor from 1uF to 10uF.
    Pull up resistor on ADPD144RI I2C line.
    [VitalX-ESP.kicad_sch]
2024-08-26 [VTX-7] Initialize GSR Block.
    Initial implementation of GSR/EDA readout circuit.
    [VitalX-ESP.kicad_sch]
2024-08-26 [nightly] ESP32-WROOM -> ESP32-S2-WROOM
2024-08-26 [nightly] Initial esp32-s2-wroom configuration.
    [VitalX-ESP.kicad_sch]
2024-08-27 [nightly] Connect peripherals.
    [VitalX-ESP.kicad_sch]
2024-08-30 [nightly] Finalize schematic, ERC exclutions.
    Exclude typical power-in power-out ERC errors.
    [VitalX-ESP.kicad_sch]
2024-08-30 [nightly] Asign footprint.
    [VitalX-ESP.kicad_sch]
2024-08-31 [nightly] Finalize schematic.
    Added power connector.
    [VitalX-ESP.kicad_sch]
2024-09-01 [nightly] Solving ERC.
    [VitalX-ESP.kicad_sch]
2024-09-01 [nightly] Initial PCB layout.
    4 layer stack up:
    - Signal
    - GND
    - GND
    - Signal
    Currently working on ECG Block.
    [VitalX-ESP.kicad_pcb, VitalX-ESP.kicad_sch]
2024-09-04 [nightly] Change ECG Probe connector.
    Utilized PJ-320D for ECG Probe connector.
    [VitalX-ESP.kicad_sch]
2024-09-04 [nightly] Inital signals routing.
    First iteration of signals (only) routing.
    [VitalX-ESP.kicad_pcb]
2024-09-06 [nightly] Change naming convertion.
    +3.3V -> +3V3.
    [VitalX-ESP.kicad_sch]
2024-09-06 [nightly] Finalize board layout.
    [VitalX-ESP.kicad_pcb]
2024-09-06 [nightly] Change ECG Probe footprint.
    Changes in accordance with reference design.
    - https://www.snapeda.com/parts/SJ2-3593D-SMT-TR/CUI%20Devices/view-part/?ref=mouser
    - https://easyeda.com/editor#project_id=8294b8a1d6874413ae900972098163d6
    [VitalX-ESP.kicad_pcb, VitalX-ESP.kicad_sch]
2024-09-06 [nightly] Resolve DRC.
    [VitalX-ESP.kicad_pcb]
2024-09-13 [nightly] Switch to through via only.
    [VitalX-ESP.kicad_pcb]
2024-09-13 [nightly] Adhere to the ECG connector standard.
    Mimic Adafruit ECG probe connector design.
    [VitalX-ESP.kicad_sch]
2024-09-15 [nighly] Various PCB update.
    PCB stack-up change: Signal-GND-Power(3.3V)-Signal
    Track width in mil: 10, 15, 20, 42
    Via size in mil(dia/hole): 20/10, 15/30
    Show ECG Probe 3D model
    Obfuscate 1.8V track
    [VitalX-ESP.kicad_pcb]
2024-09-20 [nightly] Program/Debug interface.
    Implementing proper program connector (2x3) and jtag (2x5)
    [VitalX-ESP.kicad_pcb, VitalX-ESP.kicad_sch]
2024-09-29 [nightly] Various footprint update.
    Change footprints:
    - Reset button
    - GSR conn header
    Minor PCB changes:
    - Increase thermal relief via size
    [VitalX-ESP.kicad_pcb, VitalX-ESP.kicad_sch]
2024-09-30 [nightly] Various footprint update.
    Footprint changes:
    - Boot select SMD -> Through-hole
    [VitalX-ESP.kicad_pcb, VitalX-ESP.kicad_sch]
2024-10-06 [nightly] ESP32-S2-WROOM 3d model
2024-10-06 [nightly] Finallize PCB
    Seperate Antenna ground plane
    Add grounded mounting hole
    Add logo
    [VitalX-ESP.kicad_pcb, VitalX-ESP.kicad_sch]
2024-11-19 Update for fabrication: Add top&bot layer mass, change logo, add GND vias, refine text
    [VitalX-ESP.kicad_pcb]
2025-04-14 Software update: version 0.2.0
    - Auto restart device and reset timestamp after 5 minutes of activity
    - Publish captured waveforms every 5 seconds
    - MQTT topics restructured: USER (PHONE APP) <----> HOST (.PY APP) <------> DEVICE
    - Add patient's information into .csv file
2025-04-15 Minor fix
    - remove gsr filter
    - fix wrong topic name
    - filename changed: [patient_id]_[save_duration]_[timestamp]
    - fix 5-min restart feature
    - delete firmware/ to prevent collision
2025-04-16 Software: v0.2.1
    - Dynamically update device id, mqtt topics and sampling information
    - Decode CBOR data from device and parse it to JSON
2025-04-21 Software v0.2.2
    SAMPLING_RATE correctly default to max value
    Update ECG DSP pipeline: notch 60Hz -> notch 60Hz -> ButterWorth lowpass 40Hz
    TLS now require server key
2025-05-09 Add low-pass filter warning
    Seek May 1st 2025 report slides for infomations
2025-05-14 Add reset wifi credential feature (without low-pass filtering)
2025-05-20 Adjust filter parameters
    Notch filter Q=5 for 60Hz and its harmonics
    Apply notch filter to GSR/EDA signal
2025-05-20 Code refactoring
    Encapsulate pain assessment flow into PainAssessor class
2025-05-22 Integrate pain level prediction to Qt app
    make prediction every 6 second
    prediction windows is 5.5 seconds of the most recent samples
2025-05-30 return the original device_id getting method
2025-08-13 modify filter, add signal conversion
